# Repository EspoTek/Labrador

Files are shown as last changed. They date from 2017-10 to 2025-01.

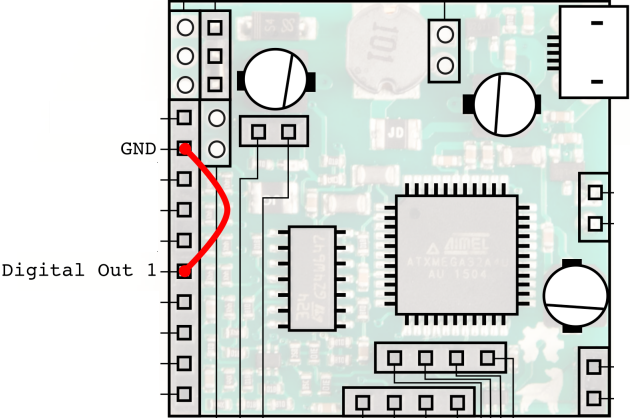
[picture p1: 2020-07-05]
Desktop_Interface/diagram.png

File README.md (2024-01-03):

# What is it?
The [EspoTek Labrador](http://espotek.com/labrador) is an open-source board that turns your PC, Raspberry Pi or Android Smartphone and into a full-featured electronics lab bench, complete with oscilloscope, signal generator and more.

This repo hosts all of the software and hardware that makes Labrador possible.

# Tutorial
If you're new to Labrador or oscilloscopes in general, I strongly recommend checking out the fantastic tutorial series produced by Lief Koepsel:   
https://www.wellys.com/posts/courses_electronics/  
It features well-written, rich articles as well as video content that explains everything more clearly than I ever could!  

# Getting Started
To download binary (executable) versions of the software, go to:  
https://github.com/espotek/labrador/releases

For the documentation, please visit:  
https://github.com/espotek/labrador/wiki 

# Raspberry Pi Build
***Please note that the 32-bit version of Raspbian version 9 (Stretch) or later is required to install this software.***

To install Labrador on the Raspberry Pi, open a terminal and paste the following command:  
`wget -O /tmp/labrador_bootstrap_pi https://raw.githubusercontent.com/EspoTek/Labrador/master/labrador_bootstrap_pi && sudo chmod +x /tmp/labrador_bootstrap_pi && sudo /tmp/labrador_bootstrap_pi`

This will automatically download, compile and install the latest version of the Labrador software from source.  The whole process will take around 20-30 minutes, so don't forget to pack a snack!  
After running it, a desktop entry will appear for the Labrador software (under Education), and running the `labrador` command from the terminal will launch the software interface.

# Additional Extras
There are community contributed 3D printable cases available at Thingiverse, courtesy of SpaceBex and Bostwickenator:
* https://www.thingiverse.com/thing:3188243
* https://www.thingiverse.com/thing:4705392

* Dave Messink has designed [a case that can be laser cut from 3mm plywood](https://github.com/EspoTek/Labrador/files/13813693/Re__Labrador_Case.1.zip)  
The binding posts and cables he used are from Amazon.  
https://www.amazon.com/dp/B07YKYP8MN?psc=1&ref=ppx_yo2ov_dt_b_product_details  
https://www.amazon.com/dp/B08KZGPTLM?ref=ppx_yo2ov_dt_b_product_details&th=1  
https://www.amazon.com/dp/B08KZGPTLM?ref=ppx_yo2ov_dt_b_product_details&th=1  



# Building from Source
If you're looking to build from source but don't know where to start, Qt Creator is the easiest way to get your toes wet!  
https://www.qt.io/download-open-source/  
When installing, make sure you tick the box to install Qt 5.15 or later.

Once it's installed, open Desktop_Interface/Labrador.pro, then Clean All -> Run qmake -> Build All.

If you're on Linux (including Raspberry Pi), then you can also build the software from source by cloning the repo, cd'ing to the Desktop_Interface directory then running:  
```
qmake
make
sudo make install
```
Then, to launch, just type `labrador` into the terminal.

On Macos, additional steps may be required.  See issue https://github.com/EspoTek/Labrador/issues/238

To build the AVR software, I use Atmel Studio 7.  Just load up the .atsln and push F7.  You can use `avr-gcc` if you don't want to install a full IDE.

The PCB files can be edited in KiCAD 5.0 or later.

# Licence
All Dekstop software files are licenced under GNU GPL v3.  https://www.gnu.org/licenses/gpl.html

All Microcontroller software files, with the exception of those provided by Atmel, are licenced under the 3-Clause BSD License.  https://opensource.org/licenses/BSD-3-Clause

All hardware files (schematics, PCB) are licenced under Creative Commons 4.0 (CC BY-NC-SA).  https://creativecommons.org/licenses/by-nc-sa/4.0/

# Collaboration
If you want to submit a Pull Request, bug report or feature request please feel free to do so here at GitHub.  
If you just want to say hello and remind me that people are actually using my product (or if you just don't want to make a GitHub account), please email admin@espotek.com

Thanks to all.  
~Chris

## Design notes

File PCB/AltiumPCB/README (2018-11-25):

Altium PCB designed by Ele4nor based on the original EspoTek KiCAD design.

This is just a prototype design optimized for homemade pcb fabrication.
The pcb design and BOM is different from "Tinylab_proto1", but the schematic is mostly Compatible.
Note that the small designators are NOT ideal and they're there for pdf only reference.
nevertheless it has been tested and functions properly but you need to program atmel usb dfu bootloader first to allow firmware flashing from Desktop App.
Use of the crystal oscillator is optional and requires firmware modification.

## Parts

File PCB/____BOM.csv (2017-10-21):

Id | Designator | Package | Quantity | Designation | Description | Notes
1 | C6,C9,C15 | c_elec_4x5.3 | 3 | CP1 | SMD Electrolytic Capacitor, 33uH 16V
2 | IC1 | LQFP-44_10x10mm_Pitch0.8mm | 1 | ATXMEGA32A4U-A | ATXMEGA32A4U-AU
3 | P2 | USB_Micro-B_WIDE | 1 | USB_OTG | Micro USB-B connector
5 | C1,C2,C7,C8,C10,C11,C13,C14,C16,C17,C18 | C_0603 | 11 | C | 1uF 0603 Ceramic Cap
6 | C3,C4,C5 | C_0603 | 3 | C_Small | 1uF 0603 Ceramic Cap
7 | D1 | SMA_Standard | 1 | D_Schottky | SMA Schottky Diode, 1.5V 1A
8 | D2 | LED_0603 | 1 | LED | 0603 LED
9 | F1 | C_1210 | 1 | F_Small | PTC Fuse
10 | L1 | SELF-WE-PD-XXL | 1 | INDUCTOR | SMD Inductor (self-wound package)
11 | L2,L3,L4 | R_1206 | 3 | INDUCTOR | SMD Inductor 1206
4 | P1,P5 | Pin_Header_Straight_1x04 | 2 | SCOPE_OUT | Female 1x4 header
12 | P3 | Pin_Header_Straight_1x04 | 1 | DIG_OUT | Stackable 1x10 Header | P3, P4 and P4 share a single header. Please do not use flimsy/weak pins!
14 | P6 | Pin_Header_Straight_1x04 | 1 | DAC_OUT | Stackable 1x10 Header | P3, P4 and P4 share a single header. Please do not use flimsy/weak pins!
13 | P4 | Pin_Header_Straight_2x02 | 1 | PDI/3V3 | Stackable 1x10 Header | P3, P4 and P4 share a single header. Please do not use flimsy/weak pins!
 | P7 | Pin_Header_Straight_1x02 | 1 | PSU | Stackable 1x2 Header | “Stackable” refers to the pins that are female on one side and male on the other, like on many Arduino shields.
16 | P8 | Pin_Header_Straight_1x02 | 1 | DIG_IN | Female 1x2 Header
17 | P10 | Pin_Header_Straight_1x03 | 1 | EXPANSION | - | Unpopulated
18 | P11 | Pin_Header_Straight_1x03 | 1 | SWITCH | Male 1x3 Header
26 | REF** | Pin_Header_Straight_1x02 | 1 | Pin_Header_Straight_1x02 | Male 1x2 Header | This will need to be soldered on upside down
19 | Q1 | SOT-23-3 | 1 | Q_NMOS_GSD
20 | R1,R2,R3,R4,R5,R6,R15,R16,R17,R18,R19,R20,R21,R22,R23,R24,R25,R26,R27,R28,R29,R30,R31 | R_0603 | 23 | R
21 | R7,R8,R9,R10,R11,R12,R13,R14 | R_0603 | 8 | 28R
22 | R32 | R_0603 | 1 | R_Small
23 | U1 | SOT-23-3 | 1 | 78L05
24 | U2 | SOIC-14_3.9x8.7mm_Pitch1.27mm | 1 | LM324
25 | U3,U4 | SOT-363 | 2 | DMN63D8LDW

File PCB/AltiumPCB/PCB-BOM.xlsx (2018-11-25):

Comment | Description | Designator | Footprint | LibRef | Quantity
Atxmega32A4U-AN |  |  | QFP44P80_1200X1200X120L60X37N | Atxmega32A4U-AN | 1
1µF | 1µF 25V Ceramic Capacitor X5R 0805 (2012 Metric) 0.079" L x 0.049" W (2.00mm x 1.25mm) | C1, C2, C3, C4, C5, C6, C11, C12, C18, C19, C20 | CAPC200X125X75L45N | 885012107015 | 11
1nF | 1000pF 16V Ceramic Capacitor X7R 0805 (2012 Metric) 0.079" L x 0.049" W (2.00mm x 1.25mm) | C7 | CAPC200X125X75L45N | 885012207033 | 1
0.47µF | 0.47µF 10V Ceramic Capacitor X7R 0805 (2012 Metric) 0.079" L x 0.049" W (2.00mm x 1.25mm) | C8, C13 | CAPC200X125X75L45N | 885012207020 | 2
0.10µF | 0.10µF 10V Ceramic Capacitor X7R 0805 (2012 Metric) 0.079" L x 0.049" W (2.00mm x 1.25mm) | C9, C21 | CAPC200X125X75L45N | 885012207016 | 2
4.7µF | 4.7µF 16V Ceramic Capacitor X5R 0805 (2012 Metric) 0.079" L x 0.049" W (2.00mm x 1.25mm) | C10 | CAPC200X125X75L45N | 885012107013 | 1
20pF | CAP CER 20PF 50V NP0 0805 | C14, C15 | CAPC200X125X75L45N | CL21C180JBANNNC | 2
CAP_POLAR | Aluminium Electrolyte 16V max | C16, C17 | Cap_Elec_47uF | CAP_POLAR | 2
FM5819-W | Schottky Diodes & Rectifiers Vr/40V Io/1A T/R | D1 | DIOM470X266X220L114X139N | FM5819-W | 1
RED | LED RED DIFFUSED 0805 SMD | D2 | LEDC200X125X38L45N | LH R974-LP-1 | 1
AO6802 | MOSFET 2N-CH 30V 3.5A 6-TSOP | IC1, IC2 | ALPHAOMEGA TSOP-6 |  | 2
Micro USB | CONN USB MICRO B RECPT SMT R/A | J1 | FCI USB 10118193-0001LF |  | 1
Jumper |  | J3, J4 | RESC200X125X50L35N |  | 2
22uH | Fixed Inductor 22uH 20% 165mA | L1, L3, L4 | CAPC200X125X140L45N | LBC2016T220M | 3
100uH | FIXED IND 100uH 400MA 1.26 OHM | L2 | CD54-Modified | CD75NP-331KC | 1
Expansion | Header, 3-Pin | P0 | HDR1X3 | Header 3 | 1
SCOPE_OUT | Header, 4-Pin | P1, P5 | HDR1X4 | Header 4 | 2
DIG_OUT | Header, 4-Pin | P3 | HDR1X4 | Header 4 | 1
PDI | Header, 4-Pin | P4 | HDR1X4 | Header 4 | 1
DAC_OUT | Header, 6-Pin | P6 | HDR1X6 | Header 6 | 1
PSU | Header, 2-Pin | P7 | HDR1X2 | Header 2 | 1
DIG_IN | Header, 2-Pin | P8 | HDR1X2 | Header 2 | 1
SWITCH | Header, 3-Pin | P11 | HDR1X3 | Header 3 | 1
2N7002 | MOSFET N-CH 60V 0.115A SOT-23 | Q1 | SOT23-3P95_230X110L30X43N | 2N7002LT1G | 1
1K | RES SMD 1K OHM 1% 1/8W 0805 | R1, R4, R5, R8, R11, R12, R13, R14, R17, R18, R19, R20, R29, R30, R31 | RESC200X125X50L35N | RC0805FR-071KL | 15
1M | RES SMD 1M OHM 5% 1/8W 0805 | R2, R7 | RESC200X125X50L35N | RC0805JR-071ML | 2
75K | RES SMD 75K OHM 1% 1/8W 0805 | R3, R6 | RESC200X125X50L35N | RT0805FRE0775KL | 2
28R | RES SMD 28 OHM 1% 1/10W 0603 | R9, R10, R15, R16, R21, R22, R23, R24, R25, R26, R27, R28 | RESC160X80X55L25N | RC0603FR-0728RL | 12
100R | YAGEO RC0805JR-07100RL RES, THICK FILM, 100R, 5%, 0.125W, 0805 | R32 | RESC200X125X50L35N | RC0805JR-07100RL | 1
AMS1117-3.3 | Linear Reg 3.3, 1.2V dropout | U1 | SOT223-4P229_700X180L36X74N | AMS1117-3.3 | 1
LM324 | IC OPAMP GP 14SOIC | U2 | SOIC14P127_865X600X175L83X41N | LM324MX | 1
8MHz | Crystals 8MHz 20pF | Y1 | TXC 9C | ATS08ASM-1 | 1

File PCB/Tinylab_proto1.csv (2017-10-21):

Reference | Value | Footprint | Datasheet
C1 | SMD MLCC 1uF 16V 0603 | Capacitors_SMD:C_0603
C2 | SMD MLCC 1uF 16V 0603 | Capacitors_SMD:C_0603
C3 | SMD MLCC 1uF 16V 0603 | Capacitors_SMD:C_0603
C4 | SMD MLCC 1uF 16V 0603 | Capacitors_SMD:C_0603
C5 | SMD MLCC 1uF 16V 0603 | Capacitors_SMD:C_0603
C6 | SMD 4mm 33uF | Capacitors_SMD:c_elec_5x5.3
C7 | SMD MLCC 1uF 16V 0603 | Capacitors_SMD:C_0603
C8 | SMD MLCC 1uF 16V 0603 | Capacitors_SMD:C_0603
C9 | SMD 4mm 33uF | Capacitors_SMD:c_elec_4x5.3
C10 | SMD MLCC 1uF 16V 0603 | Capacitors_SMD:C_0603
C11 | SMD MLCC 1uF 16V 0603 | Capacitors_SMD:C_0603
C13 | SMD MLCC 1uF 16V 0603 | Capacitors_SMD:C_0603
C14 | SMD MLCC 1uF 16V 0603 | Capacitors_SMD:C_0603
C15 | Thru Hole 6.3mm 220uF | Capacitors_ThroughHole:C_Radial_D6.3_L11.2_P2.5
C16 | SMD MLCC 1uF 16V 0603 | Capacitors_SMD:C_0603
D1 | Thru Hole Schottky 1A | Diodes_ThroughHole:Diode_DO-41_SOD81_Horizontal_RM10
F1 | SMD PTC 400mA | Capacitors_SMD:C_1206
IC1 | QFN ATXMEGA16A4U-A | Housings_QFP:LQFP-44_10x10mm_Pitch0.8mm
L1 | Thru Hole Radial 220uH | Inductors:INDUCTOR_V
L2 | SMD 10uH 1210 | Resistors_SMD:R_1210
L3 | SMD 10uH 1210 | Resistors_SMD:R_1210
P1 | Female Header 1x2 | Pin_Headers:Pin_Header_Straight_1x02
P2 | Micro USB-B Connector (F) | Connect:USB_Micro-B_WIDE
P3 | Male header 1x4 | Pin_Headers:Pin_Header_Straight_1x04
P4 | Male header 2x2 | Pin_Headers:Pin_Header_Straight_2x02
P5 | Female Header 1x2 | Pin_Headers:Pin_Header_Straight_1x02
P6 | Male header 1x4 | Pin_Headers:Pin_Header_Straight_1x04
P7 | Male header 1x2 | Pin_Headers:Pin_Header_Straight_2x02
P8 | Feamle Header 1x2 | Pin_Headers:Pin_Header_Straight_1x02
P9 | Female Header 1x2 | Pin_Headers:Pin_Header_Straight_1x02
P10 | Female Header 1x2 | Pin_Headers:Pin_Header_Straight_1x02
Q1 | SMD nMOS Transistor TSM2302CX | SMD:SOT-23-3
R1 | SMD 1M? 20V 0603 | Resistors_SMD:R_0603
R2 | SMD 1M? 20V 0603 | Resistors_SMD:R_0603
R3 | SMD 75k? 6.3V 0603 | Resistors_SMD:R_0603
R4 | SMD 75k? 6.3V 0603 | Resistors_SMD:R_0603
R5 | SMD 1k? 16V 0603 | Resistors_SMD:R_0603
R6 | SMD 1k? 16V 0603 | Resistors_SMD:R_0603
R7 | SMD 28? 6.3V 0603 | Resistors_SMD:R_0603
R8 | SMD 28? 6.3V 0603 | Resistors_SMD:R_0603
R9 | SMD 28? 6.3V 0603 | Resistors_SMD:R_0603
R10 | SMD 28? 6.3V 0603 | Resistors_SMD:R_0603
R11 | SMD 28? 6.3V 0603 | Resistors_SMD:R_0603
R12 | SMD 28? 6.3V 0603 | Resistors_SMD:R_0603
R13 | SMD 28? 6.3V 0603 | Resistors_SMD:R_0603
R14 | SMD 28? 6.3V 0603 | Resistors_SMD:R_0603
R15 | SMD 1k? 16V 0603 | Resistors_SMD:R_0603
R16 | SMD 1k? 16V 0603 | Resistors_SMD:R_0603
R17 | SMD 1k? 16V 0603 | Resistors_SMD:R_0603
R18 | SMD 1k? 16V 0603 | Resistors_SMD:R_0603
R19 | SMD 1k? 16V 0603 | Resistors_SMD:R_0603
R20 | SMD 1k? 16V 0603 | Resistors_SMD:R_0603
R21 | SMD 100? 16V 0603 | Resistors_SMD:R_0603
R22 | SMD 28? 6.3V 0603 | Resistors_SMD:R_0603
R23 | SMD 28? 6.3V 0603 | Resistors_SMD:R_0603
R24 | SMD 28? 6.3V 0603 | Resistors_SMD:R_0603
R25 | SMD 28? 6.3V 0603 | Resistors_SMD:R_0603
R26 | SMD 1k? 16V 0603 | Resistors_SMD:R_0603
R27 | SMD 100? 16V 0603 | Resistors_SMD:R_0603
R28 | SMD 100? 16V 0603 | Resistors_SMD:R_0603
R29 | SMD 100? 16V 0603 | Resistors_SMD:R_0603
R30 | SMD 100? 16V 0603 | Resistors_SMD:R_0603
U1 | SMD 3.3V Reg RT9161A-33GV | SMD:SOT-23-3
U2 | SMD LM324 | Housings_SOIC:SOIC-14_3.9x8.7mm_Pitch1.27mm
U3 | SMD DMN63D8LDW | TO_SOT_Packages_SMD:SOT-363
U4 | SMD DMN63D8LDW | TO_SOT_Packages_SMD:SOT-363

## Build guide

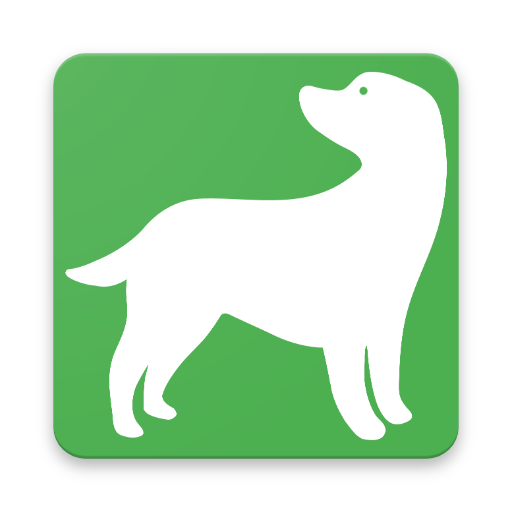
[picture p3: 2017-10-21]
Desktop_Interface/build_android/package_source/res/web_hi_res_512.png

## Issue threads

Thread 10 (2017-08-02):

### ISSUE TITLE
Make the PCB a little more breadboard compatible?

### ISSUE THREAD

**Issue by tardate** [EspoTek/Labrador#10]
I've been playing with a batch 1 backer edition PCB (you can [see my notes here](https://github.com/tardate/LittleArduinoProjects/tree/master/Equipment/Labrador)).

I was able to stick it on a breadboard with a minor bend of the PSU pins, and then the PSU is on the breadboard power rail and all the pins on the left side of the board are routed to the breadboard. This is pretty convenient for testing and experimentation.

Although the board will never be fully breadboard-compatible in its current form, there's one minor change that might be worth considering: nudge the PSU pins up or down 50mil and then the PCB would plug directly into a standard MB104 breadboard with no pin bending.

**Comment by EspoTek** [comment]
You're absolutely right.   I didn't actually believe you until I tried it myself!
The fact that the pins bend when being plugged into a breadboard is definitely a bug.  Fortunately not a critical one, but still not ideal...  It was designed to go in smoothly; I even used a 50mil grid to ensure it was perfectly accurate.  Looks like at some stage that grid god messed up, though.

I'll have to fix that up for the next batch (also will ensure they use a better opamp to reduce noise a bit).

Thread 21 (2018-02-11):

### ISSUE TITLE
Feature request: Enable data storage in Android app

### ISSUE THREAD

**Issue by drtrigon** [EspoTek/Labrador#21]
Please add data recording/storage/logging to the Android app, would that be possible?

(edit: what about the power supply features - could them be added too?)

**Comment by EspoTek** [comment]
Power supply and data storage functions are actually all in the software.  I just hide the buttons to activate them on Android.

The reason I did this is because of the small memory on most phones.  8GB free space or less is very common, and that would fill up with something like 10-15 mins of recording.

The power supply option is disabled since USB OTG is specced for 100mA only, and most of that would be eaten up just by the board itself.  I think I calculated 65mA with no signal generator or power supply load, leaving only 35mA for the power supply (which would be almost completely lost in the switching circuitry).

That being said, I plan on improving the DAQ features of Labrador, and once that's in then I'll be able to add the data storage back into Android.
I'll be working on it during the week after Christmas.

Enabling the power supply is not really an option, though.

**Comment by ajxn** [comment]
Maybe give a short not about this in a About message dialog?

**Comment by drtrigon** [comment]
> The reason I did this is because of the small memory on most phones. 8GB free space or less is 
> very common, and that would fill up with something like 10-15 mins of recording.

What about a screenshot feature; store the contents of the display - e.g. single trigger - as png or csv?

What about an expert feature that unhides the hidden features with a warning about the issues.

> The power supply option is disabled since USB OTG is specced for 100mA only, and most of that 
> would be eaten up just by the board itself. I think I calculated 65mA with no signal generator or 
> power supply load, leaving only 35mA for the power supply (which would be almost completely lost 
> in the switching circuitry).

I assumed something like that... that's a pitty because it would be useful not as a current source but signal voltage source, e.g. for testing a ADC port (drawing microamps).

> That being said, I plan on improving the DAQ features of Labrador, and once that's in then I'll be 
> able to add the data storage back into Android.
> I'll be working on it during the week after Christmas.

Great news, perfect! Will be a very nice (Christmas) gift!

**Comment by EspoTek** [comment]
The screenshot feature is also already in there.  It's hidden on Android too, but I can't offer a good explanation why...

I could enable an "Expert Mode" that turns on all of the features, and it could pop up with ajxn's "About" message that warns the user when you click it!

**Comment by drtrigon** [comment]
Can you give an assumption when the new updated app will be available?

**Comment by EspoTek** [comment]
When I get around to it.  ;)
Should be soon.

Have quit the PhD and so will be unemployed as soon as I finish a piece of software for the honours students.  We have a neurosignal amplifier only runs on a single PC that runs Windows XP and requires a DRM dongle.  I managed to reverse-engineer the protocol, but now that needs to be turned into an API.
Then, it's Labrador time.  :)

**Comment by EspoTek** [comment]
It's live.
You should get a notification from Google Play soon.

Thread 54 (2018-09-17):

### ISSUE TITLE
Nice to have; more sophisticated scaling options

### ISSUE THREAD

**Issue by drtrigon** [EspoTek/Labrador#54]
As we have the scaling options on the main window now it would be really really nice to polish them a bit.
1. up and down arrows should change the decimal place the cursor is (currently it just in- or decrements by 1.0 volt or second which is most of the time way to much)
2. may be add sliders or knobs that resemble more the look and feel of a desktop scope (don't know what the GUI toolkit/framework offers)

This is not a bug but a nice to have feature of low priority. Thanks.

**Comment by EspoTek** [comment]
I've actually got a class that does point number one already; its the one used in the Signal Generator inputs (which honestly could use a bit of a spit-polish too).  Changing this should be pretty easy.

Honestly not keen on sliders or knobs on the main screen, though.  One of the selling points is that it doesn't have them!  I've used the Hantek software before, which tried to simulate the interface of a "real" scope and honestly it was just really clunky.

**Comment by EspoTek** [comment]
Check the latest patch.  The changes I made also improved the signal generator controls and the pop-up dialog.

Let me know what you think.
For now, I'm very happy with everything (although a "time minimum" and "time max" might be better than "time window" and "delay".

I'm closing this issue for now, as I don't think more controls are necessary.  You already have direct range controls on the front page, after all.  :)

**Comment by drtrigon** [comment]
Thanks for your work! Hmmm - honestly to me it is a bit confusing ... but it might be that I am not used to it yet. It is smoother and makes more sense when you are looking for a signal you don't know the scaling yet. May be a little confusing is the fact the when is written "500mV" I actually have to enter "0.5[ENTER]". Let me work with it for some time... It is clearly better that before.

One thing you should check the behaviour for negative values, crossing "-1.0V" and values below does not work properly. I also had other strange issues. E.g. if I put the cursor into the field "-500mV" (which is default when starting) and hit [ENTER] it changes to "500mV" (positive).

**Comment by EspoTek** [comment]
You should be able to type in "500m[ENTER]" to get 500mV.  I just tested it in my machine and that was the case.

Issue with negative numbers noted.  There's an internal variable keeping track of the last known correct input that is not being updated correctly (with sign).  I'll fix this and patch now.

**Comment by EspoTek** [comment]
Oh, and one last thing: regarding why you must press enter now:
Say the user wants to enter "500mV".  They type in 5, then 0, 0, m.

If you recalculate the scale on every keypress, it first goes to 5V, then 50V (which goes down to the maximum of 20V because it's invalid), then 200V (which again is reduced to 20V to stay within the valid range), then 20mV.  That is not 500mV.

If you're just trying to get a rough estimate and don't need to be precise, I'd recommend using the mouse scrolling.

**Comment by drtrigon** [comment]
> You should be able to type in "500m[ENTER]" to get 500mV. I just tested it in my machine and that was the case.

You are right - guess I entered "500mV[ENTER]" not beeing aware that the "V" stays there and then it jumps to 20V... ;)

Having to press enter is ok and makes sense - I don't like the updates on every keypress (exactly due to issues you describe - some value need more than 1 char to be expressed...)

> If you're just trying to get a rough estimate and don't need to be precise, I'd recommend using the mouse scrolling.

I was not aware of mouse scrolling (now I even got my "knob")! This is great; very useful and fast!!

> I have fixed the issue with negative values. It now uses std::abs() to compare work out the units and scale things, as opposed to the weird hack it was using before.

Thanks for this, however still some non-intuitive things happening here:
- if I press enter in the field the result heavily depends on the cursor position before pressing enter - I assume only the value in front of the cursor is used (e.g. if I put the cursor behind the 5 of -500mV I do get -5V)
- if I start scrolling with the mouse wheel downwards (starting from -500mV) it does 1V steps - I think this is just an issue of a missing init step
- if I start scrolling upwards the same for one step (+1V to 500mV) then it behaves as expected - seems to be sign dependent
- if I try to scroll down from 500mV (passing 0) it stops working at 90mV and the only way to make it work again is entering a value by keyboard

**Comment by EspoTek** [comment]
Wow.  And that's why you don't write code on the train after a day of work while sleep deprived!

I've fixed all of the bugs you mentioned, done some more testing to try and find others and it looks like it's all fixed now.  The error regarding the very small (near-zero) number is an issue with floating point precision.  I won't launch into the details, but it's basically a weird, weird form of rounding error.  I've seen an example of it once where a guy managed to get the result 1 + 1 = 3!

**Comment by drtrigon** [comment]
What I tested seems to work nicely now even "10us" works - cool, thanks!

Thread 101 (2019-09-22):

### ISSUE TITLE
Cannot See Device When Plugged In (Mac 10.14.8, RPi Zero)

### ISSUE THREAD

**Issue by joedski** [EspoTek/Labrador#101]
Hello, I am not seeing my Labrador when I plug it into my computer.  I have tried the following, both with nothing shorted and in bootloader mode.

- Mac 10.14.8 on 2012 MBP:
   - USB 2 port directly on computer
   - USB 3 port on dock
- Raspberry Pi Zero W:
   - Data-enabled USB port
   - Data-enabled USB port via USB 2 hub, Labrador as only device plugged into the hub

Across all of the above, I've tried:

- In bootloader mode
- Not in bootloader mode

Using `lsusb` did not show any changes before and after plugging the device in.  The power LED does turn on, but I don't see anything else happen anywhere.  I've ensured that the cable I used can transmit data, as I have used it to interface with a NodeMCU board.

Is there anything else I could try that I might have missed in the docs?

**Comment by EspoTek** [comment]
If `lsusb` shows no change and the cable can transfer data, then the only possible explanation is that your board is DOA.

Please contact me at `admin@espotek.com` with your order info and I'll have a replacement shipped out to you free of charge.

And thanks for being descriptive with all the troubleshooting steps - no back and forth this way.

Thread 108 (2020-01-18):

### ISSUE TITLE
higher sample rate to see adressable LED data. SPI, I2C, Serial.

### ISSUE THREAD

**Issue by perigalacticon** [EspoTek/Labrador#108]
This would be a perfect device to use to diagnose addressable led data such as WS2812B, but it runs at 800kHz.  Can't tell you how many times I wanted to get a good look at what is causing glitching in certain installations.  Having a small battery or 5V powered portable scope would be great for this.  Not sure how fast you need to sample to get 800kHz but that would be really nice.

**Comment by EspoTek** [comment]
Try Labrador's logic analyzer.  It works exactly like the oscilloscope, but takes 3 million samples per second (so you'd get 3-4 samples per bit at 800kHz!)

The downside is that each sample is only one bit - so you can't see the exact analog waveform of the signal, just if it's on or off.

If you need that level of detail in a portable device, I've heard nothing but positive things about Picoscope's products:
https://www.picotech.com/
They're obviously a bit more than $29, though!

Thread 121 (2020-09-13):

### ISSUE TITLE
taking samples for both channels simultaniously via librador

### ISSUE THREAD

**Issue by jhegedus42** [EspoTek/Labrador#121]
Hi,

I am able to get samples from a single chanell using a single octave call via librador.

Now, the question is ... how can I get samples for two channels ?

I am trying to understand this : https://github.com/EspoTek/Labrador/blob/e7c5e4e68768f87d1df8cc61be07e32e3b8d232e/Librador_API/___librador/librador_shared_library/o1buffer.cpp

and this : 

but its not easy ... 

https://github.com/EspoTek/Labrador/blob/e7c5e4e68768f87d1df8cc61be07e32e3b8d232e/Librador_API/___librador/librador_shared_library/usbcallhandler.cpp

maybe if I could modify this : https://github.com/EspoTek/Labrador/blob/e7c5e4e68768f87d1df8cc61be07e32e3b8d232e/Librador_API/___librador/librador_shared_library/usbcallhandler.cpp#L313

to do something like this : https://github.com/EspoTek/Labrador/blob/e7c5e4e68768f87d1df8cc61be07e32e3b8d232e/Librador_API/___librador/librador_shared_library/usbcallhandler.cpp#L76

but what is isocallback ? I am really sorry for all these dumb questions but C/C++ is something I never was able to 
learn :( ... I try to read the code... but it's difficult.

can someone please point me into the right direction ? Please ?
 
I am really lost here ... :(

Thanks,

Jozsef

**Comment by phr0gger** [comment]
I have some python code to configure the Labrador board and to read back data.
Would that help you?

**Comment by EspoTek** [comment]
When the device is set to mode 4, the latter 375 bytes of the each packet contain the data for CH2.
https://docs.google.com/document/d/1ZDO1RTarQTNB6Pdfi_T4YukL51oYan_kk_teb1cu6-o/edit#heading=h.3v1s22knpngz

**Comment by jhegedus42** [comment]
> I have some python code to configure the Labrador board and to read back data.
> Would that help you?

Thank you that would be great, is it on github ? I check your code now.  Maybe it is already there.

**Comment by phr0gger** [comment]
I don't think my code is GitHub-worthy.
Below is what I did on my Raspi to read and plot data from the Labrador board with Python 3.7. It is based on the sample code by Vincent Pelletier, who wrote the python-libusb1 package which you need for the asynchronous support.
PyUSB does not support asynchronous isochronous transfers.

`import usb1  # python-libusb1 package from 
from struct import unpack
import sys
import time
import numpy as np
import matplotlib.pyplot as plt

MODE = 0  # Labrador mode ( 7: 12 bit 375 ksps, 6: 8 bit 750 ksps, 0: 8 bit 375 ksps)
SHOW = 20*750

VENDOR_ID = 0x03eb
PRODUCT_ID = 0xba94
INTERFACE = 0
TIMEOUT = 100

GAIN = 0x0808  # gain 4: ±6V
#GAIN = 0x0c0c  # gain 8: ±3V

ISO_EP = 0x81
NUM_ISO_PACKETS = 66
ISO_PACKET_SIZE = 750
TRANSFER_COUNT = 4

def processReceivedData(trf):
    global stream
    global t0
    if MODE == 7:
        dt = np.dtype(np.int16)
        dt = dt.newbyteorder('<')  # big endian
    else:
        dt = np.dtype(np.int8)
    t1 = time.monotonic()
    if trf.getStatus() != usb1.TRANSFER_COMPLETED:  # TRANSFER_COMPLETED = 0 
        # Transfer did not complete successfully, there is no data to read.
        # This example does not resubmit transfers on errors. You may want
        # to resubmit in some cases (timeout, ...).
        print(' Error: Transfer not completed successfully!')
        return
    stream.extend( np.frombuffer(trf.getBuffer(), dtype=dt)) 
    #stream.extend( trf.getBuffer())  # raw hex stream
    # trf.getActualLength() useless for isochronous (always 0)
    print(f' time: {1000*(t1-t0):3.2f}')  
    # Resubmit transfer once data is processed for endless process
    #transfer.submit()
    t0 = t1

stream = []
with usb1.USBContext() as context:
    context = usb1.USBContext()
    handle = context.openByVendorIDAndProductID(
        VENDOR_ID,
        PRODUCT_ID,
        skip_on_error = True,
    )
    if handle is None:  # Device not present, or user is not allowed to access device.
        print('Error: Cannot find Labrador Board!')
        sys.exit()
    else:
        print('Found', handle.getManufacturer(), handle.getProduct())
        print(' FW Version :', unpack('H',handle.controlRead(0xc0,0xa8,0,0,2,TIMEOUT))[0])
        print(' FW Variant :', handle.controlRead( 0xc0, 0xa9, 0, 0, 1, TIMEOUT)[0])
            
    with handle.claimInterface( INTERFACE):  # Required to receive/send data.
        handle.controlWrite( 0x40, 0xa5, MODE, GAIN, b'', TIMEOUT) #
        handle.controlWrite( 0x40, 0xa6, 0, 0, b'', TIMEOUT)  # turn off digital pins
        handle.controlWrite( 0x40, 0xa4, 0, 0, b'', TIMEOUT)  # disable DAC amp
        handle.controlWrite( 0x40, 0xa3, round(6/18.15*128)-1, 0, b'', TIMEOUT)  # set 6V

        # Build a list of transfer objects and submit them to prime the pump.
        transfer_list = []
        for i in range( TRANSFER_COUNT):
            print( ' Starting transfer',i)
            transfer = handle.getTransfer( NUM_ISO_PACKETS)  # libusb_alloc_transfer
            transfer.setIsochronous(                         # libusb_fill_iso_transfer
                ISO_EP,
                NUM_ISO_PACKETS*ISO_PACKET_SIZE,             # 
                callback = processReceivedData,
            )                                                # default is no timeout
            transfer.submit()                                # libusb_submit_transfer
            transfer_list.append(transfer)
        print()
        t0 = time.monotonic()
        # Loop as long as there is at least one submitted transfer.
        while any(x.isSubmitted() for x in transfer_list):
            try:
                context.handleEvents()                      # libusb_handle_events
            except usb1.USBErrorInterrupted:
                pass
if MODE == 7:
    data = -np.right_shift( stream, 4)[:SHOW]
elif MODE == 6:
    #data = list(map(lambda x: -x, stream[:SHOW]))
    data = stream[:SHOW]
elif MODE == 0:
    data = np.reshape(stream[:2*SHOW],(4*SHOW//750,375))[::2].ravel()
fig, ax = plt.subplots(figsize = (12, 7))
ax.plot( data, '.', markersize = 2)
ax.set_xticks(range(0,len(data)+1,375))
ax.grid()
ax.set_title( f'Mode: {MODE}, Gain: 0x{GAIN:04X}')
fig.tight_layout()
plt.show()  
`

**Comment by jhegedus42** [comment]
Thank you !

It seems to work !

![image](https://user-images.githubusercontent.com/6671476/87711164-31f7a300-c7a7-11ea-9e61-ad9f7b5fce40.png)

**Comment by jhegedus42** [comment]
> I don't think my code is GitHub-worthy.
> Attached is what I did on my Raspi to read and plot data from the Labrador board with Python 3.7. It is based on the sample code by Vincent Pelletier, who wrote the python-libusb1 package which you need for the asynchronous support. Note, that PyUSB does not support asynchronous isochronous transfers, read and write are blocking.


Would it be ok to use blocking calls?

C itself is blocking - if using Librador.

Why is it good to use async lib?

I mean, why is it bad if one python process is blocking?

I plan to use TCP/IP to transfer packets read from Labrador to Simulink/GNURadio, that can be blocking, python runs in separate process.

I did this already with UDP packets using Librador library from C. It worked for one channel. Using python seems to be easier though.

But do I need async calls for that?

It just worked fine with Librador + blocking calls to libusb + C + UDP + Simulink + FIFO (buffer).

Is async USB transfer with callbacks any better than blocking calls ?

It seems more complicated.  

Is the Labrador QT GUI using async USB calls or just using blocking USB calls + buffer + 2 threads (one for GUI and one for USB transfers).

Cheers,

Jozsef

**Comment by EspoTek** [comment]
I think I can answer that question, Joszef.

The GUI code uses async isochronous USB (but synchronous everything else), and the main advantage of this is no data loss when streaming.
The board itself only stores the previous 1ms of data in SRAM, so in order to extract every sample it must be polled every single USB frame - no exceptions.
This is impossible to guarantee with synchronous communications, as there is some downtime between packets being received and packets requested.
The flow looks something like this:
 1) Request _n_ frames of data
 2) Data received 
 3) Process data
 4) Goto 1
If steps 2 and 3 take longer than 1ms, you lose continuity.

With async, you can immediately queue a second (future) request after the first request is submitted.  Then, when the first request is complete, you can schedule a third before the second completes (and so on...).  This way you don't lose continuity.

Try looking at an odd frequency (I like 912Hz) and you'll see what I'm talking about.  You'll get a discontinuity every `NUM_ISO_PACKETS` samples.

(Apologies if that made no sense.  I just became a father on Saturday and haven't had a nights' sleep since)

**Comment by jhegedus42** [comment]
Dear Chris,

First of all. I wish you and your family health and happiness !

Thank you for the help. It is very good to know this. It's not trivial to make such a 
little device work. I start to understand that.

I rather ask now @phr0gger ... he may not be so busy now.

Is there a way to make this record data continously ?
The python code that you attached, @phr0gger  ?

What does it mean 
"  # Build a list of transfer objects and submit them to prime the pump."


"prime the pump" ?

Do you mean bootstrap ?

I was thinking I should uncomment this line : 

```
    # Resubmit transfer once data is processed for endless process
    #transfer.submit()
```
but it just died...

or did not really work...

what should I do if I want to continously capture data and, say, send them over
TCP/IP or just save to file ?

Cheers,

Jozsef

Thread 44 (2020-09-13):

### ISSUE TITLE
DataLogger for Education

### ISSUE THREAD

**Issue by drtrigon** [EspoTek/Labrador#44]
As requested in #37 a new issue:

>> Another point here is; if the device would be a bit more fool-prove and the software a bit more intuitive to use (e.g. "beginner" mode) we could use it in schools for education (for teenagers, ~14yrs). Again all concurring products are about 10 times the price of a labrador. At least I would be immediately willing of ordering 10 to 20 devices for one school I am working at. :)
> 
> Drtigon, the hardware is actually designed to be foolproof. You can short any pin to any other pin and guarantee no damage. It's also difficult to break with external sources. You can hook up 18V directly to the signal generator, for example, and the only thing that will burn is one of "fuse" resistors which can be easily replaced with a blob of solder. Even if you can't solder, only the one output you damaged will become faulty; the rest will work OK.
> 
> Not really sure what I could do to make the software easier to use, but open to suggestions (please create a separate issue though)!

I am thinking of something like
* Vernier Logger Pro: https://www.vernier.com/products/software/lp/
* Vernier DataQuest™ Software for TI-Nspire™: https://www.vernier.com/platforms/texas-instruments/software/data-collection/dataquest/

Basically both have a play/stop button to start/stop capturing of data. The data is shown in a table (time series) and in an plot. Additionally the software has a database for sensors available to be able to have the correct ranges, units, etc. ready. This database could be something simple like an ini file.

> Send me an email at admin@espotek.com and I can get you a good deal on a class set, especially if you're happy to share educational materials you make. :)

This is the direction I am thinking of. ;))

**Comment by EspoTek** [comment]
Hey, sorry about the late response.  Have just been ridiculously overwhelmed at work.

The software idea looks pretty cool, but I don't have the time to develop it myself right now.  There's an API that just needs a bit of polishing up before release, though, and that could be used to make software like this.  Are you any good at programming?

Cheers,
~Chris

**Comment by drtrigon** [comment]
> Are you any good at programming?

I can solve issues by programming (python, c/c++) - but I would not talk about "how good I am"... ;) Would it be possible to release the API - even if it is not polished yet?

**Comment by EspoTek** [comment]
Of course.  It's been part of the main tree for a while.
https://github.com/EspoTek/Labrador/tree/master/Librador_API

Note that it's Linux-only for the moment.

**Comment by EspoTek** [comment]
Oh, and here's a full user guide.  
https://docs.google.com/document/d/11Cu6602X_y5x0IwIBZnP7ImIx0jykX7AzToh83-7hCM/edit?usp=sharing

It's basically public-beta ready.

**Comment by drtrigon** [comment]
Cool! Thanks a lot! Greetings

**Comment by EspoTek** [comment]
^^ Wow, that is a lot of ICs for a fairly similar device to the Labrador.  I think I've got two chips with more than 3 pins?

**Comment by drtrigon** [comment]
So let's do it better ... correct?

**Comment by EspoTek** [comment]
You mean a higher end Labrador 2.0?  If only I had the time!

**Comment by drtrigon** [comment]
Let's start and do it step-by-step. What's the first point? Specs and search for key parts?


Am 10. Februar 2019 00:39:33 MEZ schrieb Chris Esposito <notifications@github.com>:

**Comment by EspoTek** [comment]
Yep, that's the first step.  Important features are a High-speed USB 2.0 transceiver (not full-speed, which is annoying 1/40th the speed of high speed!), fast ADC, DMA and good documentation/support.
I remember reading about a MCU that had all of these features, but it cost around $7 per IC (compared to $2 for the Labrador 1.0's XMEGA32A4U).
Once I've picked a part I'd need to make sure that the software is basically plausible.
Next step would be to redesign the analog front-end.  6 resistors and half an LM324 won't cut it for higher frequency/bandwidth.  Finally, all of the software - both embedded and fixing the desktop software to get it to work with the new hardware.

Completely doable, but would be a massive investment of time which I would honestly rather put towards marketing Labrador 1.0 - at least for 2019.
It's a great product, but I only sell a few of them a week.  I think a big part of that is because I'm not getting out there and letting people know that it exists.  Both times it was reviewed in a magazine I sold 30-40 in the space of 2 weeks, and that was before the site redesign and eBay/Amazon listings (I was selling maybe 2-3 a week then, compared to 4-5 now).  More marketing materials (e.g. a demonstration video on the website) and some tutorials/educational materials would help a lot too.  \
At the end of the day, I'd honestly rather have 10,000 users with Labrador 1.0 than 2,000 users with Labrador 1.0 and another 2,000 users with Labrador 2.0.  Both in terms of business, and in terms of making a difference in electronics education, the more people that have access to hardware, the better.

**Comment by drtrigon** [comment]
Thanks for the insight!

> More marketing materials (e.g. a demonstration video on the website) and some tutorials/educational materials would help a lot too. 

Exactly what came to my mind... I am Physicist so let's brainstorm about that. With Labrador only, you can do power consumption measurement of e.g. a phone, a quadcopter, ... else?
For education or school some additional sensors might be needed.

Currently I work in a technical highscool that started a new program 3 years ago. My boss did and still does at least 1 visit for promo a week (for 3 years now). I also do some, why not for Labrador also? Good thing here in Switzerland the Labrador cost about the price of 3-4 boxes of cigarettes - so it's really affordable.

**Comment by ajxn** [comment]
My 2nd year Computer Engineering students have a project that could be to
design a prototype for a GUI in Java or something like that.
To bad it is in the winter, so that project course has already passed. Next
time maybe?
 If I don't contact you about that in september, you are welcome to contact
me to see what we can do. :-)

Den ons 13 feb. 2019 kl 23:15 skrev Chris Esposito <notifications@github.com
>:

> Yep, that's the first step. Important features are a High-speed USB 2.0
> transceiver (not full-speed, which is annoying 1/40th the speed of high
> speed!), fast ADC, DMA and good documentation/support.
> I remember reading about a MCU that had all of these features, but it cost
> around $7 per IC (compared to $2 for the Labrador 1.0's XMEGA32A4U).
> Once I've picked a part I'd need to make sure that the software is
> basically plausible.
> Next step would be to redesign the analog front-end. 6 resistors and half
> an LM324 won't cut it for higher frequency/bandwidth. Finally, all of the
> software - both embedded and fixing the desktop software to get it to work
> with the new hardware.
>
Wouldn't an embedded ARM M0 CPU be good for a more high end Labrador 2.0?
They are also popular in Maker space, like the ATXMEGA32 is. There are
great small embedded chips which would fit your description. Might have a
look at USB 3 for higher speed transfer, if possible in the cost frame.
Faster and more memory then the ATXMEGA32A4U 8-bit chip.
That is, something like ARM M0 core at 48MHz with DMA, 12 bit ADC and USB
and a nice price of about €1.16 for 100:
https://www.mouser.se/datasheet/2/389/stm32f070c6-956182.pdf

Might even show up as a USB memory stick where it simulated files that can
be used to read samples from, and write commands to configure the
Labrador.  Might make the software for hosts a bit easier to write?
The firmware for Microbit uses that approach to download and reprogram it,
open source that is.

Oh, so much fun project and so little time. :-)

> Completely doable, but would be a massive investment of time which I would
> honestly rather put towards marketing Labrador 1.0 - at least for 2019.
> It's a great product, but I only sell a few of them a week. I think a big
> part of that is because I'm not getting out there and letting people know
> that it exists. Both times it was reviewed in a magazine I sold 30-40 in
> the space of 2 weeks, and that was before the site redesign and eBay/Amazon
> listings (I was selling maybe 2-3 a week then, compared to 4-5 now). More
> marketing materials (e.g. a demonstration video on the website) and some
> tutorials/educational materials would help a lot too.
> At the end of the day, I'd honestly rather have 10,000 users with Labrador
> 1.0 than 2,000 users with Labrador 1.0 and another 2,000 users with
> Labrador 2.0. Both in terms of business, and in terms of making a
> difference in electronics education, the more people that have access to
> hardware, the better.
>
Know nothing abut marketing, sorry.  :-)

And yes, please ignore as I am just armchair coding here. But would be nice
to hear about what you might think about those thoughts. You that actually
have done the work with Labrador.

/Jackson

**Comment by EspoTek** [comment]
> Exactly what came to my mind... I am Physicist so let's brainstorm about that. With Labrador only, you can do power consumption measurement of e.g. a phone, a quadcopter, ... else?
> For education or school some additional sensors might be needed.

Yeah, agreed.  Labrador on its own is not super exciting.  An experiments book that you can use with a cheaply available, common kit from AliExpress/eBay (or perhaps even my own home-made kit, if I were to be a better businessman) would really drive home the educational possibilities of Labrador, and perhaps something that you eventually build up into a 3D printed robot would be even cooler.  You could really show off the advantages of having a scope there, with AC measurements on the power supply rails before/after R/L filtering, direct reads on sensors so people can actually understand what the code is doing and more.  Again, though, this all takes time.  Perhaps I should talk to my employer about working 4 days a week.  Not being entirely un-serious there.

> Currently I work in a technical highscool that started a new program 3 years ago. My boss did and still does at least 1 visit for promo a week (for 3 years now). I also do some, why not for Labrador also? Good thing here in Switzerland the Labrador cost about the price of 3-4 boxes of cigarettes - so it's really affordable.

Not quite sure what you mean here?  As in visit the high school and try to sell the Labrador to students?  Or teachers?  I've sold some boards at a group of guys who do Microcontroller stuff once, and that went pretty well (about 20 in one night, can't complain), but I'm just not quite sure how to break into education without first developing at least some basic teaching aids.

**Comment by drtrigon** [comment]
> Perhaps I should talk to my employer about working 4 days a week. Not being entirely un-serious there.

As I am studying (still!) and because of family, I am working 3 days per week only.

> Not quite sure what you mean here? As in visit the high school and try to sell the Labrador to students? Or teachers? I've sold some boards at a group of guys who do Microcontroller stuff once, and that went pretty well (about 20 in one night, can't complain), but I'm just not quite sure how to break into education without first developing at least some basic teaching aids.

Schools, Students and Teachers are good customers for sure, but I thought more general e.g. fab labs, maker spaces but also enthusiasts and public in general. My focus is on the promo, you have to go out there in order to reach the people. As often as possible, e.g. once a week.

**Comment by EspoTek** [comment]
> My 2nd year Computer Engineering students have a project that could be to design a prototype for a GUI in Java or something like that. To bad it is in the winter, so that project course has already passed. Next time maybe? If I don't contact you about that in september, you are welcome to contact me to see what we can do. :-)
Oh, that would be grest.  Please send me an email at admin@espotek.com so I can contact you about it in September (unless you don't mind posting your email on a public forum!)

> Wouldn't an embedded ARM M0 CPU be good for a more high end Labrador 2.0? They are also popular in Maker space, like the ATXMEGA32 is. There are great small embedded chips which would fit your description. Might have a look at USB 3 for higher speed transfer, if possible in the cost frame. Faster and more memory then the ATXMEGA32A4U 8-bit chip. That is, something like ARM M0 core at 48MHz with DMA, 12 bit ADC and USB and a nice price of about €1.16 for 100: https://www.mouser.se/datasheet/2/389/stm32f070c6-956182.pdf Might even show up as a USB memory stick where it simulated files that can be used to read samples from, and write commands to configure the Labrador. Might make the software for hosts a bit easier to write? The firmware for Microbit uses that approach to download and reprogram it, open source that is. Oh, so much fun project and so little time. :-)

Actually, the CPU and RAM don't matter much for Labrador - almost all of the actual processing is done on the user's PC and that's easily 100x the FLOPpage (technical term) of a 32-bit ARM Cortex M0.  Actually, if you look at the code for the XMEGA, the CPU does nothing apart from initialise the hardware and events system, acknowledge USB commands and calibrate the clock.  Everything is driven by the events system and DMA, so the most important specs are ADC sample rate and DMA throughput.  CPU-independent triggering is a necessity too.

I've looked at the STM32 series before and they are almost perfect for my purposes.  The F3 series can have up to 4 ADCs at 5Msps each (ie 20Msps total), but you cannot add USB 2.0 high-speed to it.  The F2 and F4 series allow you to add USB 2.0 High-speed PHYs, but the ADC only samples at 2Msps.  Both have plenty of DMA bandwidth, as well as built-in opamps and a 2-channel DAC.  Price is low too.  If only the F3 did USB HS!!!

Not quite sure how I'd work with files as the samples need to come in as a continuously updated stream.  At the moment, it uses a double ring buffer to store everything but to work with files I'd need to continuously update and stomp older files.  It does actually make sense to use HDD or SSD to increase the size of the buffer above and beyond the users' RAM though, and I could even add this to Labrador 1.0! 

> Know nothing abut marketing, sorry. :-) And yes, please ignore as I am just armchair coding here. But would be nice to hear about what you might think about those thoughts. You that actually have done the work with Labrador. /Jackson
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

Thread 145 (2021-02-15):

### ISSUE TITLE
Device not connected and other issues

### ISSUE THREAD

**Issue by hchaudh2** [EspoTek/Labrador#145]
I have tried to download Mac OS Continuous Build from this link: https://github.com/EspoTek/Labrador/releases
however, I am unable to open Labrador application. So I downloaded Mac OSX from this link https://github.com/EspoTek/Labrador/releases/tag/1.1  and it opens however when I try plugging in usb to calibrate, it says device not connected. I have even tried firmware recovery and multiple USB cables especially those that support data transfer. I'm using an adapter so I only have one USB port on it so one device is connected at a time. But even then it says device is not connected. I'm using this for an electric circuits class in college and have a deadline for a lab report. So, can you help me out please? What is the issue here?

**Comment by EspoTek** [comment]
Can you please give me the output of `lsusb` when the board is connected?

You can install it and run it through Homebrew:
```
/bin/bash -c "$(curl -fsSL https://raw.githubusercontent.com/Homebrew/install/HEAD/install.sh)"
brew install lsusb
lsusb
```

**Comment by hchaudh2** [comment]
I had already downloaded Homebrew earlier today. But this is what I got when I connected the board. 

>huriyyah@Huriyyahs-MacBook-Pro-2 ~ % lsusb
2021-02-13 00:12:00.434 system_profiler[10794:200635] SPUSBDevice: IOCreatePlugInInterfaceForService failed 0xe00002be
2021-02-13 00:12:00.434 system_profiler[10794:200635] SPUSBDevice: IOCreatePlugInInterfaceForService failed 0xe00002be
2021-02-13 00:12:00.435 system_profiler[10794:200635] SPUSBDevice: IOCreatePlugInInterfaceForService failed 0xe00002be
2021-02-13 00:12:00.435 system_profiler[10794:200635] SPUSBDevice: IOCreatePlugInInterfaceForService failed 0xe00002be
2021-02-13 00:12:00.436 system_profiler[10794:200635] SPUSBDevice: IOCreatePlugInInterfaceForService failed 0xe00002be
2021-02-13 00:12:00.436 system_profiler[10794:200635] SPUSBDevice: IOCreatePlugInInterfaceForService failed 0xe00002be
2021-02-13 00:12:00.436 system_profiler[10794:200635] SPUSBDevice: IOCreatePlugInInterfaceForService failed 0xe00002be
Bus 000 Device 001: ID 05ac:1018 Apple Inc. USB3.1 Hub  Serial: DLC01230154KD56A2
Bus 020 Device 001: ID 05ac:1017 Apple Inc. USB2.0 Hub  Serial: DLC01230154KD56A2
Bus 020 Device 003: ID 03eb:a000 Atmel Corporation USBGobindar Dummy Device 
Bus 020 Device 002: ID 05ac:1463 Apple Inc. USB-C Digital AV Multiport Adapter  Serial: DLC01230154KD56A2
Bus 128 Device 000: ID 05ac:8102 Apple Inc. Touch Bar Backlight  Serial: 0000000000000000
Bus 128 Device 000: ID 05ac:8302 Apple Inc. Touch Bar Display  Serial: 0000000000000000
Bus 128 Device 000: ID 05ac:027f Apple Inc. Apple Internal Keyboard / Trackpad  Serial: FM702860219N1R1A2+RWN
Bus 128 Device 000: ID 05ac:8103 Apple Inc. Headset  Serial: 000000000000
Bus 128 Device 000: ID 05ac:8262 Apple Inc. Ambient Light Sensor  Serial: 000000000000
Bus 128 Device 000: ID 05ac:8514 Apple Inc. FaceTime HD Camera (Built-in)  Serial: CC20272G4LHJ3Y328
Bus 128 Device 000: ID 05ac:8233 Apple Inc. Apple T2 Controller  Serial: 0000000000000000
Bus 000 Device 001: ID 1d6b:CITR Linux Foundation USB 3.1 Bus 
Bus 000 Device 001: ID 1d6b:0003 Linux Foundation 3.0 root hub 
Bus 000 Device 000: ID 05ac:8102 Apple Inc. Apple T2 Bus 
huriyyah@Huriyyahs-MacBook-Pro-2 ~ %

**Comment by hchaudh2** [comment]
I had already downloaded Homebrew earlier today. But this is what I got when I connected the board.

2021-02-13 00:12:00.434 system_profiler[10794:200635] SPUSBDevice: IOCreatePlugInInterfaceForService failed 0xe00002be
2021-02-13 00:12:00.434 system_profiler[10794:200635] SPUSBDevice: IOCreatePlugInInterfaceForService failed 0xe00002be
2021-02-13 00:12:00.435 system_profiler[10794:200635] SPUSBDevice: IOCreatePlugInInterfaceForService failed 0xe00002be
2021-02-13 00:12:00.435 system_profiler[10794:200635] SPUSBDevice: IOCreatePlugInInterfaceForService failed 0xe00002be
2021-02-13 00:12:00.436 system_profiler[10794:200635] SPUSBDevice: IOCreatePlugInInterfaceForService failed 0xe00002be
2021-02-13 00:12:00.436 system_profiler[10794:200635] SPUSBDevice: IOCreatePlugInInterfaceForService failed 0xe00002be
2021-02-13 00:12:00.436 system_profiler[10794:200635] SPUSBDevice: IOCreatePlugInInterfaceForService failed 0xe00002be
Bus 000 Device 001: ID 05ac:1018 Apple Inc. USB3.1 Hub Serial: DLC01230154KD56A2
Bus 020 Device 001: ID 05ac:1017 Apple Inc. USB2.0 Hub Serial: DLC01230154KD56A2
Bus 020 Device 003: ID 03eb:a000 Atmel Corporation USBGobindar Dummy Device
Bus 020 Device 002: ID 05ac:1463 Apple Inc. USB-C Digital AV Multiport Adapter Serial: DLC01230154KD56A2
Bus 128 Device 000: ID 05ac:8102 Apple Inc. Touch Bar Backlight Serial: 0000000000000000
Bus 128 Device 000: ID 05ac:8302 Apple Inc. Touch Bar Display Serial: 0000000000000000
Bus 128 Device 000: ID 05ac:027f Apple Inc. Apple Internal Keyboard / Trackpad Serial: FM702860219N1R1A2+RWN
Bus 128 Device 000: ID 05ac:8103 Apple Inc. Headset Serial: 000000000000
Bus 128 Device 000: ID 05ac:8262 Apple Inc. Ambient Light Sensor Serial: 000000000000
Bus 128 Device 000: ID 05ac:8514 Apple Inc. FaceTime HD Camera (Built-in) Serial: CC20272G4LHJ3Y328
Bus 128 Device 000: ID 05ac:8233 Apple Inc. Apple T2 Controller Serial: 0000000000000000
Bus 000 Device 001: ID 1d6b:CITR Linux Foundation USB 3.1 Bus
Bus 000 Device 001: ID 1d6b:0003 Linux Foundation 3.0 root hub
Bus 000 Device 000: ID 05ac:8102 Apple Inc. Apple T2 Bus

**Comment by EspoTek** [comment]
I see the issue now: it enumerates as `Bus 020 Device 003: ID 03eb:a000 Atmel Corporation USBGobindar Dummy Device`.
There was a firmware issue with one particular batch of the boards produced last year, as well as a hotfix for this firmware issue in the newest version of the desktop software.

If you're able to connect your board to another PC running the latest version of the desktop software, the firmware will be fixed on your board and the board will connect in future.  If you don't have another PC, a VM should work too.

**Comment by hchaudh2** [comment]
It worked! Thank you for that! Also what should I do if my multimeter in labrador is not working. I'm unable to click on anything like for example: I'm trying to change the mode to I, but I cannot do that.

**Comment by hchaudh2** [comment]
It worked! Thank you for that!

**Comment by EspoTek** [comment]
Good to hear, and sorry about the runaround.
Regarding the multimeter issue, read "A Note on Buffers" here:
https://github.com/EspoTek/Labrador/wiki

You'll need to turn off the oscilloscope before you can turn on the multimeter.

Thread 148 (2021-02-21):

### ISSUE TITLE
Scope reads 4.5Vdc but multimeter reads 3Vdc

### ISSUE THREAD

**Issue by macktion** [EspoTek/Labrador#148]
Hi. I'm monitoring a small 4.5Vdc 1A PSU used on some tiny Christmas lights.  The Labrador zoomed-in shows quite smooth 4.5 (0v offset)but the multimeter shows only approx 3.15V max/min/RMS.  shouldn't the scope and meter values be close?  

I also haven't had luck measuring current with the Lab. trying to verify/improve the accuracy of the 200Ma I measured with my discrete meter that created a significant/unwanted series load that dims the lights. I could not even get the Lab to allow the string of lights to turn on while indicating current as high as 1.5A at 0ohms series.

**Comment by EspoTek** [comment]
The multimeter measures the difference between CH1 and CH2.  If nothing is attached to CH2, it'll float towards VCC/2 (around 1.65V).
Please see documentation here:
https://github.com/EspoTek/Labrador/wiki

Current measurements with a low burden voltage is not a standard feature of most multimeters, including Flukes.
It's possible to use an external amplifier circuit to lower burden voltage to near-zero, though.
Dave Jones did a video on it a while back:
https://www.youtube.com/watch?v=jx0dryLmUEQ

**Comment by macktion** [comment]
Thank you.  Very helpful.

**Comment by lkoepsel** [comment]
This issue is happening for me. If one follows the following process, it is easy to replicate.
1. Open Labrador application, press M to bring up Range Dialog and change Vmax to 5V.
2. Connect Oscilloscope CH1 to Power Supply (Positive) and Oscilloscope CH2 to Power Supply (GND) *Note the CH1 line is about 4.8V and is solid, no noise.*

![Screen Shot 2021-03-27 at 7 38 46 AM](https://user-images.githubusercontent.com/7906684/112724224-8f63f800-8ecf-11eb-872b-a5502aad5934.png)

3. Uncheck Oscilloscope CH1 and check Multimeter, all of the values (Max, Min, Mean and RMS) will be identical and incorrect. In this case, 2.96V. *Note CH1 line has now moved to 2.96V, continues to be solid, no noise*

![Screen Shot 2021-03-27 at 7 34 55 AM](https://user-images.githubusercontent.com/7906684/112724269-c934fe80-8ecf-11eb-886f-a8ab03d95912.png)

4. Uncheck Multimeter and check Oscilloscope then check Paused and uncheck Paused. *Note the CH1 line moves up to 4.9V and once Paused is unchecked, the line appears with a slight amount of noise*
5. Uncheck Oscilloscope and check Multimeter and the values:
     * Are correct when compared with a DMM
     * Are not all identical, they vary with a little bit of noise.
 
![Screen Shot 2021-03-27 at 7 35 25 AM](https://user-images.githubusercontent.com/7906684/112724181-41e78b00-8ecf-11eb-9975-4d2970f861f6.png)

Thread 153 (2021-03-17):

### ISSUE TITLE
How to Connect Labrador to Computer

### ISSUE THREAD

**Issue by ddd15dd** [EspoTek/Labrador#153]
Hi, I am using a USB to microUSB cord to connect the labrador to my laptop, and the Red LED light lights up. But when I open the software it says Device Not Connected. For my circuits lab, it says that I should calibrate it before plugging the Labrador into the breadboard. But when I try to do that I get an error message "You need to connect the board before calibrating it!"

Please help!

**Comment by EspoTek** [comment]
Please see the troubleshooting guide here:
https://github.com/EspoTek/Labrador/wiki/Troubleshooting-Guide

The most common issue I hear about is caused by people using a USB cable without data lines.  When you use that same cable to connect a USB device (such as an Android phone) to your computer, is that device detected?

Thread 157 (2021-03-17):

### ISSUE TITLE
help measuring current in multimeter mode

### ISSUE THREAD

**Issue by khtodd1** [EspoTek/Labrador#157]
Hello.  I'm trying to use Labrador to measure the gate current when switching on a MOSFET from an output of a microcontroller.  I've read the Wiki 500 times but I'm not still not quite sure how to connect it to measure what I want.  Can you please explain, or even better, throw up a quick circuit sketch?  Thank you.

**Comment by EspoTek** [comment]
Unfortunately, I don't think it's a simple task for a device such as this to measure MOSFET gate currents as they're likely to be in the nA range.
However, if you could, the circuit diagram would like like this:
![IMG_8859](https://user-images.githubusercontent.com/22040436/111422374-b3427380-8742-11eb-9471-5c4e0f4ebf88.JPG)
A load resistor is placed in series with the current you want to measure, and the two channels of the scope are added across the load.

The software interface looks like this:
<img width="770" alt="Untitled" src="https://user-images.githubusercontent.com/22040436/111422443-d3723280-8742-11eb-9d94-0e8e1c83b8df.png">
Set the multimeter mode to "I" and manually enter the value of the series resistance (load resistor from circuit diagram) into the box shown.

Sorry if I can't be of more help.  If you're really keen to measure something that small, maybe consider looking to the uCurrent or similar?

**Comment by khtodd1** [comment]
Thank you for your help with this - it's a power MOSFET - so the gate
current could actually get up to 100mA or so, although I'd like to see it
on the order of 10-15mA.  I will try your suggestion.

**Comment by EspoTek** [comment]
Ahh, of course.  You should have no issue then.

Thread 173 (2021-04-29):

### ISSUE TITLE
External Scope probes?

### ISSUE THREAD

**Issue by kevinpowell** [EspoTek/Labrador#173]
Breadboard mounting is fine, but I'm more likely to put the Labrador in a small enclosure and wire up a couple bnc connectors for a traditional scope probe.  Would there be any issues doing this?  Will a standard tektronix (1x and 10x) probe work well?

**Comment by EspoTek** [comment]
Hi Kevin, you'll have absolutely no issues with this.  It's quite common for people to do this, and there are even 3D printable enclosures on Thingiverse with holes for BNC probes.

Good luck with the projects, and feel free to send pics when you're done.  Always like seeing what people get up to!

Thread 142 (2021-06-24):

### ISSUE TITLE
"Calibrate on connection" calibrates on all reconnections.

### ISSUE THREAD

**Issue by maith1** [EspoTek/Labrador#142]
We are using the Labrador for a class electric circuits lab. Our instructions were to create a simple circuit on a breadboard with two wires and a resistor. After doing this, the Labrador shuts off and then wants to recalibrate again. This basically forces me into an infinite loop of recalibration. Is my Labrador broken or could I be doing something wrong?

**Comment by EspoTek** [comment]
Which OS are you using?  The calibration routine is completely managed by the PC and has nothing to do with the hardware.

**Comment by maith1** [comment]
I am using Windows 10. The calibration seems to go just fine before I plug anything in but once I form a full circuit, the red light on the device shuts off. When I unplug it and plug it back in, it wants to calibrate again.

**Comment by EspoTek** [comment]
OK, so it looks like there's two independent issues here.
The first issue is a minor software bug - it seems that asking it to calibrate when the board is connected (on initial launch) will ask it to calibrate _every_ time the board is connected.  Relaunching the software will fix this.

The second issue is most likely caused by an short somewhere in your circuit.  Please check it very, very carefully, and make sure you're aware how the breadboard is laid out.

**Comment by maith1** [comment]
I have installed the software on another computer entirely and am still encountering the same problem. My circuit appears to be constructed more or less the same as the one our lab tutorial shows as well. I'm not sure what could be causing this other than maybe a faulty Labrador?

**Comment by EspoTek** [comment]
If the light turns off, it means the OCP is tripping.  Either the factory installed a bad fuse (which can be routed around), or there is an issue with the circuit.  Please send me some pics of your attached circuit and I can map out where the short is for you.

**Comment by maith1** [comment]
![File_000](https://user-images.githubusercontent.com/5343409/107583674-411dc280-6bc9-11eb-8f57-63acefc4bde6.jpeg)
I am relatively new to doing this kind of stuff so it is highly likely that I am doing something incorrectly. I just set this up the way that my lab instructions appeared to show. I'm sorry if the problem is obvious and I'm missing it.

**Comment by EspoTek** [comment]
OK, I can see what's going on here.
Honestly, the problem is obvious to a trained engineer but everyone (myself included) makes this exact kind of error when starting out.

Check out the chart here:
https://www.electronics-tutorials.ws/resistor/res_2.html

The questions to ask yourself are the following:
 - What is the resistance value of the resistor?
 - How much current is it drawing?
 - How much power is being dissipated by it?
 - How does this value compare to the max power that Labrador can supply?

(Obviously it's a leading question, but I recommend doing the maths anyway.  The magnitude differences are pretty impressive!)

**Comment by maith1** [comment]
Thank you for the helpful information. I will try to work this out now that I know where to start. I believe now that I can close this ticket. Thank you once again! Sorry for the inconvenience.

**Comment by EspoTek** [comment]
I think it's best to leave the ticket open.  While the disconnect wasn't a bug in Labrador, the re-calibration over and over again definitely was!

**Comment by maith1** [comment]
Okay! I'm not too familiar with the GitHub ticket system so I'm not really sure of the implications of opening and closing tickets but if you believe it should stay open then I trust your judgment. If I have any more problems then I guess I'll put them here. Thanks again.

**Comment by EspoTek** [comment]
Abandoning this issue.  It's low priority and honestly a mess of a system to fix.

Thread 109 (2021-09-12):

### ISSUE TITLE
flashing device firmware locks up

### ISSUE THREAD

**Issue by perigalacticon** [EspoTek/Labrador#109]
Upon installation of latest interface program on windows 10 pc, and connecting the scope, the program reports "flashing device firmware" but it gets stuck here for at least 15 minutes and appears to be locked up.

**Comment by EspoTek** [comment]
I just downloaded the latest version on my machine and plugged in a board with older firmware.  The firmware flash completed in a couple of seconds.

I suspect something else may have changed on your system, or something has happened to the board.
Please restart your PC, and then try the "Firmware Recovery" option from the "Help" menu of Labrador.

**Comment by perigalacticon** [comment]
Thanks.  Here's exactly what happens.  If I plug in the board before starting the program a notification window pops up asking for calibration.  It doesn't matter what I choose, the program then fails to start.  When launch it again (from my desktop) it asks to calibrate, again my choice doesn't affect the result but then it starts and shows device not connected.  If I then re-plugin the board it goes to flashing device firmware, and nothing I do changes that message and the scope does not run but the controls seem to react very slowly as if it is bogged down doing something.  

If I launch the program before connecting it still asks to calibrate, again my choice does not affect it and the only difference is the program launches the first time.  

I tried the firmware recovery help option, it says it appears to be configured so the problem could be the USB set up.  So I plugged the USB into various USB ports, including a USB hub I have that has the blue USB ports mentioned.  Nothing has changed the behavior of the launch process I described.

**Comment by EspoTek** [comment]
Odd.  Did it used to work in an older version of the software?

Under `C:\Program Files\EspoTek\EspoTek Labrador\firmware` you should see a batch file called "flash.bat".  If you set the board to bootloader mode (see https://github.com/EspoTek/Labrador/wiki) and then run that batch file, does it fix things?

**Comment by phr0gger** [comment]
I have seen Labrador showing a (bogus?!) Flashing Firmware message on the Raspberry Pi 3B+. 
It happens when restarting the Labrador software (but not unplugging the board) after there were -9 errors (unixUsbDriver::usbSendControl FAILED with error LIBUSB_ERROR_PIPE). The board supposedly reports FIRMWARE VARIANT = 0x00 and the software attempts to flash the board. However, the USB driver is still not working and nothing happens. One needs to power cycle the board to re-initialize the USB driver.

**Comment by 99Phish** [comment]
Terribly sorry for resurrecting an old thread.


Im afraid I am in the same boat as op.  I have the software running on my windows work pc, Albeit an older version. I also have it running on macOS after the recent continuous build update (the one after 9/2/21).

I am now just installing the software fresh on my personal pc only to encounter "flashing device firmware" without resolution..

This board has saved my hide in the field more than once so I am not complaining.  I just thought I should document the problem. I also tried plugging in the board before and after I start the software. All to the same effect. 

On my work pc and my work macbook, sometimes I need to unplug and replug the usb cable to get the software to recognize the controller on boot up.  After a single power cycle it always gets recognized and hums along as well as expected.

I seem to be running into a driver problem based off of device manager. The first image "flashing" is what I encountered after plugging in the device.

The second image "reinstalled" is what I encountered after reinstalling the current windows build. 

 ![reinstalled](https://user-images.githubusercontent.com/39873285/132972990-94053a41-b80f-4950-af38-69e0be5b9d10.png)

![Flashing](https://user-images.githubusercontent.com/39873285/132972874-6bacc04f-c2c1-47b3-b024-cdd13b706a1a.png)

--later on--

I happen to have my macbook pro with me and  connecting the labrador to that computer also results in failure. This time I am being prompted to connect the device.  

The problem is likely on my end all things considered.  I typically keep the board in my backpack in the original packaging. Pink foam and the esd bag.

**Comment by EspoTek** [comment]
Hi mate, that's very bizarre.  I suspect it's a hardware fault, but it could also possibly be a bad flash.

The first thing I'd do is to see if the board enumerates correctly when in bootloader mode.
To do this, connect Digital Out 1 to GND then reconnect your board:
https://github.com/EspoTek/Labrador/wiki/Pinout

You should see an "Atmel ATXMega32A4U" device in Device Manager if the bootloader is good.

If that works, you can go to C:/Program Files/EspoTek/EspoTek Labrador/Firmware and run the files "wipe.bat" then "flash.bat".  They should take a couple of seconds each to run (if the window immediately closes, that's not good) and the board should be back to normal.

If that doesn't work, I'd recommend trying a different cable.  If it's not the cable, contact me at admin@espotek.com and we can look into getting a replacement sent to you.

Cheers,
~Chris

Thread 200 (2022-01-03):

### ISSUE TITLE
Raspberry Pi 4b - "Calibration has been abandoned due to out-of-range values"

### ISSUE THREAD

**Issue by fluxsauce** [EspoTek/Labrador#200]
Good news - I can calibrate with Windows 10 without issue! I'm assuming the unit itself is fine.

Difficulty - I can't get it to calibrate on a Raspberry Pi 4b, Raspberry Pi OS with desktop 5.10.

The device detects and connects. The software seems to be working correctly, other than this calibration step?

I had to struggle a bit to get it installed, https://github.com/EspoTek/Labrador/issues/197 mentions it and the workaround is what I did (honestly, after Googling first, then I found the issue 😆)

Raspberry Pi firmware is current, upgraded as part of this process. I also used a breadboard to ground it, same effect, so it's not an intermittent connection. I'm using a dedicated USB-C power supply (Canakit) connected to a nicely grounded circuit so I'm assuming that's not it either.

Steps to reproduce:

![PXL_20211220_010136172 MP](https://user-images.githubusercontent.com/976391/146698317-ad3d31f9-0da7-4d26-8b80-abeef87d0f3c.jpg)
![PXL_20211220_010142160](https://user-images.githubusercontent.com/976391/146698318-557fea84-4f7d-4344-a903-a7d1c488ac80.jpg)
![PXL_20211220_010153736](https://user-images.githubusercontent.com/976391/146698319-289a9002-7d64-4a40-aeea-419e9d3b1b7e.jpg)
![PXL_20211220_010203852 MP](https://user-images.githubusercontent.com/976391/146698320-de449f95-fc31-4c02-a44d-e460925bfa7f.jpg)
![PXL_20211220_010226382](https://user-images.githubusercontent.com/976391/146698321-af50dfb1-26a8-4da4-a8a9-c59843c82005.jpg)
![PXL_20211220_010230658](https://user-images.githubusercontent.com/976391/146698323-77ddf824-34c0-4aa5-9f2b-2023c032c6b0.jpg)
![PXL_20211220_010240404](https://user-images.githubusercontent.com/976391/146698324-5f02b04e-298d-48ad-bd4d-f0f75da27fab.jpg)

With debug:

```
DEBUG MODE ACTIVE
unified debug is of size 27
...
Changing workspace...
Calibration routine beginning!
unified debug is of size 27
...
VRef (CH1) =  1.50071
VRef (CH2) =  1.4656
unified debug is of size 27
...
unified debug is of size 27
VMeasured (CH1) =  0.379172
VMeasured (CH2) =  0.369023
...
```

Thanks!

**Comment by EspoTek** [comment]
Any idea what those big bursts of noise are on the trace in pics 1 and 2?

**Comment by fluxsauce** [comment]
Breadboard jumpers were connected to the Labrador.

Nothing connected except USB cable:

https://user-images.githubusercontent.com/976391/146708428-9f58b94f-8845-4714-9db5-1380510ebee9.mp4

**Comment by EspoTek** [comment]
OK, that makes more sense.  Looking at the log, it seems like it detected a higher value than expected in the second stage.  Perhaps you lost contact temporarily, just before pressing OK?

**Comment by lchen198** [comment]
I am having the same issue on raspberry pi 4 and tried multiple times without luck.  It works fine on Win 11.

...
genericUsbDriver dectructor entering
genericUsbDriver dectructor completed
Reinitialising USB driver!
Making USB Driver invisible!!
pipeID 0 = 129
Generic Usb Driver setup complete
unixUsbDriver created!
ReinitUsbStage2 is returning
deviceConnectedDisplay::connectedStatusChanged running!
CHECKING CONNECTION!
Entering unixUsbDriver::usbInit
Libusb context initialised
Device found!!
KERNEL DRIVER INACTIVE
Interface claimed!
Connected
BOARD IS RUNNING FIRMWARE VERSION 0x0006
EXPECTING FIRMWARE VERSION 0x0006
FIRMWARE VARIANT = 0x02
EXPECTED VARIANT = 0x02
Connecting now!
deviceConnectedDisplay::connectedStatusChanged running!

...

unified debug is of size 27
unified debug is of size 27
unified debug is of size 27
VMeasured (CH1) =  0.466232
VMeasured (CH2) =  0.467766
unified debug is of size 27
unified debug is of size 27
unified debug is of size 27

**Comment by StriderTR** [comment]
I'm having the same issue, mine seems to read a constant 1.6V, but fails at the grounding. I tried grounding several ways, even to my PC's PSU.

I am also using mine with a Pi 4, same setup as the OP. My Pi 4 is in a Argon M.2 case. If I figure it out, I'll post it. :)

**Comment by theblaz** [comment]
Having the same issues but with the Linux AppImage on an x86 computer. Could there be an issue with the Linux reading values? Calibration works from windows application

**Comment by EspoTek** [comment]
I've had several reports of this bug across all platforms, and can't for the life of me reproduce it on any of my systems at home.  It seemed to appear about 2-3 months ago, and can disappear randomly too.  I'm not sure what the source of this could be, but it might be best to just roll back some patches from the past few months.

**Comment by theblaz** [comment]
thanks for the update. I'll keep playing with it.

**Comment by lchen198** [comment]
Maybe try a different USB cable?  I haven't tried it yet but I wonder if connecting the ground pin on the board with raspberry pi ground pin would help.

**Comment by theblaz** [comment]
I tried several different cables and different ports as well as different
machines. The consistency seems to be Linux as I am able to get it to work
in windows. I haven't tried it on a Mac yet.

**Comment by StriderTR** [comment]
Nice to see it's not just me. 

I tried 4 different USB cables as well as different grounding methods. I  have not tried on my Windows machine yet, haven't had time. 

I can say that the "noise" you see in the OP, I see as well, I just assumed it was when my skin touched the wires. That's what led me to try different grounding methods, I was assuming it was seeing static through those thin jumper wires. Still, same problem.

**Comment by EspoTek** [comment]
The noise is a separate issue, and not something I've seen outside of the Pi (again, not critical and not something I'm able to reproduce with my Pi 3, so I haven't spent too much time looking into it)!

The common thing that people seem to be is the trace freezing after a few seconds, then coming back after the scope is enabled/disabled.

**Comment by StriderTR** [comment]
Would it have anything to do with how the Pi is grounded? If I am not mistaken, the Pi grounds via HDMI to your monitor/TV. Not the same as your PC. Though I tried grounding mine to my PC and PSU chassis and got the same result. I'm just spitballing ideas, it's been a long day. lol

**Comment by EspoTek** [comment]
Genuinely no idea.  "Hard to reproduce" and "not critical" means I'll probably never know, sorry!

**Comment by theblaz** [comment]
I downloaded the Linux Legacy Appimage and I was able to calibrate no problem. Thanks for the suggestion and help.

**Comment by StriderTR** [comment]
Sadly, I don't see a way to get a legacy app image for Pi. Is it available anywhere?

Also, I did ground my Pi to my PC case with one of the GPIO grounds, it did affect the reading, but calibration still failed. Oh well, it was an idea. 

![lab-noground](https://user-images.githubusercontent.com/97561185/150282107-c3f1fe52-403c-4f8f-8c19-e6edfe28c8cf.jpg)
![lab-ground](https://user-images.githubusercontent.com/97561185/150282142-2899a162-9d3b-4a05-9259-b47249507675.jpg)

**Comment by EspoTek** [comment]
Finally had a bit of a lightbulb moment!
I think I know if not why, but at least when the issue was caused, and that it's part of the software.  I'll get a patch ready over the coming few days to roll back some of the changes that may have caused this regression!

**Comment by StriderTR** [comment]
Excellent! I'll give it a try once it's available. :)

**Comment by EspoTek** [comment]
It should be fixed now (keyword: should)!

Long story short, the patch that added the frequency spectrum was doing a whole lot of unnecessary maths when it wasn't enabled and overloading the Pi's tiny CPU, causing it to miss timing contraints.

I've pulled this out of the regular path (it now only runs when the spectrum mode is enabled) and it seems to be back to normal, at least from my end.

If other people are able to confirm this, I can fully close this off once and for all!

**Comment by StriderTR** [comment]
Calibration Successful!

Thanks for the fix! The Pi's tiny processor, and I, thank you! :P 

Perfect timing, the rest of the parts I ordered are arriving today so I will be able to give the Labrador a proper home. BNC connectors and probes for the scope, Banana connectors and probes for the multimeter and logic, and a clamp speaker type terminal block for the signal generator. All going in a simple black project enclosure. Once I have it all done I can take a nice pic and drop a proper review on Amazon.

Again, thanks for all your help! It's been greatly appreciated.

![2022-01-23-120333_1920x1080_scrot](https://user-images.githubusercontent.com/97561185/150692053-e1c4f92d-9b9d-47e9-a8bc-6779020ab317.jpg)

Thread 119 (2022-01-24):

### ISSUE TITLE
Working on Win 10 - but not on Android 8.0

### ISSUE THREAD

**Issue by Fixador** [EspoTek/Labrador#119]
Hi, fine on Win 10  , but using via an known good OTG into (1) Android 8.0 on a ZL10, and (2) Titan 4 . Android 5.01. The OTG lead was tested on both androids into a mouse. Labrador reports on both of the Androids  at the top of the screen that device not connected - red led is illuminated on pcb. Suggestions please

**Comment by superfrink** [comment]
Not sure if it is the same issue but I had to try four different micro USB cables until finding one that worked.

The setup was Android 9 with USB C -> OTG adapter to USB A -> USB cable to micro B -> Labrador.

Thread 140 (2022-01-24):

### ISSUE TITLE
Thought about making a more robust device/version 2?

### ISSUE THREAD

**Issue by cweagans** [EspoTek/Labrador#140]
The Labrador is great. It's really a huge accomplishment to have gotten it out the door, especially with how much functionality is packed into such a tiny space!

Have you thought about making version 2? And/or have you thought about making v2 a bigger/more full featured all-in-one device? I've been noodling on this and I think there's a pretty good market in the $100-200 range for a combination power supply/signal generator/oscope/logic analyzer. Here's my wishlist in the event that you're thinking about going down this road:

* Include a case with real ports for the various functions -- current device is good for breadboards and the like, but it would be cool to turn this into a bench tool. Display isn't needed, but having real ports for probes, PSU output, etc. would be cool!
* Bigger -- the current device is very portable, but is also easily lost in e.g. a pile of papers or whatever. Having a bigger, more substantial device would be awesome.
* More channels/higher data rate/etc -- generally just "more" across the board as it relates to the oscope/logic analyzer. I realize this wasn't ever meant to be a top-of-the-line device, but I'm curious about how far in that direction something like this could go with a bit more headroom in the budget? What's a sane number of channels/sample rate/etc?
* Same software -- the desktop client is really, really wonderful and I'd love to keep using it
* Fully variable PSU output - 0-60V up to 100W (which would allow for powering any PoE device, I think). Bonus points for making it possible to do more than one output for powering more complicated devices?
* USB-C -- I threw out all of my micro USB cables several years ago and now only have one for the Labrador. It would be awesome to standardize on USB-C across the board (and might help to accommodate higher sample rates and such too?)

That's most of my list, I think. If you're thinking about doing something like this, I'd love to collab on the software bits. Hardware isn't my forte just yet, but I'm learning.

**Comment by EspoTek** [comment]
The short answer is "yes, eventually".

Although I'd take the current software out the back and put a bolt through its skull before updating it for future hardware.  There are a lot of really short-sighted design choices that worked, but make it difficult to maintain long term.

**Comment by cweagans** [comment]
Fair enough! If you want help with the software bits, definitely hit me up. I’ve been very, very happy with Flutter and Dart if you’re looking for an alternative to the current setup.

**Comment by EspoTek** [comment]
The plan was actually to use Dear ImGui.
I'm not sure if you've used it before, but with a little bit of wrapper code to handle windowing and stuff cross-platform, it makes almost every class of GUI-related problem disappear.

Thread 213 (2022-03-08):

### ISSUE TITLE
'Batch 1' board "bricked" - scope not running

### ISSUE THREAD

**Issue by DeeJay** [EspoTek/Labrador#213]
I have a Batch 1 board purchased March 2018. I seem to have 'broken' it.

Yesterday I had it working with the current (Jan 2022) Windows continuous release of the Labrador software. (Should  have been content with that... )

Then I tried a build of Labrador for RasPiOS Bullseye 64-bit running on an RPi4B2G board. The Desktop interface appeared but reported "Device not detected". I did not investigate this in detail. 

Since then I have been unable to use the Labrador board with the previously-working MS Windows 10 installation. I have (apparently) successfully forced a Firmware Recovery by grounding the required pin and using the Help menu Recovery  option. But the 'scope function doesn't seem to run ('random' noise appears briefly then freezes) and attempts to calibrate always fail with a report of readings out of range. 

I have also tried reverting the Windows software to the legacy Update 1  and Update 2 releases,  but with no improvement. 

I think I have read all the relevant Documentation and tried all the Troubleshooting and Recovery tips. It feels as though  I have got the on-board processor into a state where it is no longer running correctly but cannot be reset?

Is there anything else I can do to breathe life into the little guy, or is this going to be a 29$ fix?

**Comment by EspoTek** [comment]
Hi mate, sounds like a bog standard bad flash.  Completely recoverable.

If you can get the board into bootloader mode, check out the two batch files under C:/Program Files/Espotek/EspoTek Labrador/Firmware

Run wipe.bat, then flash.bat and it should spring back to life.
If not, remove the wires that force it into bootloader mode then reconnect it twice.

If that doesn't fix it, shoot us an email and we can work it out together.

**Comment by DeeJay** [comment]
Just a brief comment to acknowledge that I mis-diagnosed my own problem.

I can confirm that the board itself is fine: the inability to run the 'scope - or any other data acquisition - seems to be a quirk in running the Windows interface on my Windows10 laptop.

I am in touch with  Chris via email to try to get a better understanding of why my HW/OS platform isn't being cooperative.

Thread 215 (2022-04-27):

### ISSUE TITLE
new board, after calibrate channel 1 always read around 1.667 volts and multimeter reads new 9v Alkaline at 10.1v

### ISSUE THREAD

**Issue by Mclute0** [EspoTek/Labrador#215]
am I missing something or am I getting stray voltage from somewhere?

my cheap multimeter reads the 9v battery at 8.7v, pretty sure 10.1v is just wrong.

AC coupling brings channel to zero.

the voltages below are all means.

touching the channel one probe to the USB ground show -0.12v

touch channel on to channel 2 no changes both on they both read 1.667v.

channel one to board + rail show 4.748v

channel one to - rail shows -0.03v

channel one multimeter to board - rail shows -1.6v with channel two to + rail also read 0.04 
channel one multimeter to board + rail shows 3.16v with channel two to - rail also reads 4.84

both channels read a ~60hz background oscillation at around .01 volts.

**Comment by EspoTek** [comment]
Hi mate, can you please attach a screenshot showing the 10.1V battery?

**Comment by Mclute0** [comment]
when first connecting the 9V battery, it always reads 3V for all three with no swings, but when I use the mouse wheel to scroll in or out it starts reading the 10V on a new battery and 7.9V on an older used battery with a +-0.02 volt swing.

![image](https://user-images.githubusercontent.com/101496003/159510660-7d895918-8808-4dcf-8013-12f8e6e21fe7.png)

**Comment by EspoTek** [comment]
Ahh, I see.  Make sure the trace is visible on the display; otherwise you may get issues with the amplifiers clipping.

**Comment by EspoTek** [comment]
And just to confirm, this is with CH1 (DC) on the positive terminal, and CH2 (DC) on the negative?

**Comment by Mclute0** [comment]
yes,  CH1 (DC) on the positive terminal, and CH2 (DC) on the negative. I also have not been able to get the interface to show uF. I,V,R show up, but changing to C and I get no F listed in the output stays at whatever the last reading was liike mV mA or resistance.

maybe I will take a look at the code and see if I see any issues, I used to do a little debugging for a living.

**Comment by Mclute0** [comment]
I is now giving F? without the μ? no numbers are sowing but minus sign comes are goes.

I see the display code and it looks pretty clean. I would guess this is a problem with the redraw data on window change procedures, that's without looking though all the code. still looking... The debug is showing cap_x1 == -1 that I take means no/bad reading from the board but it is transferring data of some kind.

![image](https://user-images.githubusercontent.com/101496003/159824202-ff02a688-91ab-4f5f-b20a-466a93b4ae98.png)

**Comment by EspoTek** [comment]
You'll need to set a resistance value to use R/C mode.
Please see the "Multimeter" section here:
https://github.com/EspoTek/Labrador/wiki

Cheers,
~Chris

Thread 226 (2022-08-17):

### ISSUE TITLE
Device will only measure 3 volts

### ISSUE THREAD

**Issue by JvilleJTW** [EspoTek/Labrador#226]
Trying to test my Labrador. Comparing it against my DMM on a simple circuit with an LED and resistor driven by a lab supply of 9 volts DC. DMM correctly shows 7.6 volts across resistor. Labrador in Multimeter mode shows 3V consistently. Using CH1, CH2 and Gnd. terminals hooked up to test leads. I have tried increasing voltage headroom, but this appears to only affect the onboard voltage supply. Neither DC scope channel makes any sense either. Using a Mac laptop.

**Comment by EspoTek** [comment]
Hi mate.  This isn't so much as a bug as questionable UI design.  Zoom out the scope trace so that the analog waveform is visible at 7.6V, and the digital display should start updating with the correct values too.

**Comment by JvilleJTW** [comment]
Chris--

This makes no sense. Neither the multimeter nor the scope are reading the correct figures. It's not close; they are off by 4-5 volts. I am abandoning this project.

JTW

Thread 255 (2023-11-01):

### ISSUE TITLE
Waveform generation clock settings

### ISSUE THREAD

**Issue by dbsamithey** [EspoTek/Labrador#255]
I think that line 219 of genericUsbDriver.cpp should be changed from 
`return CLOCK_FREQ / (division * channelData.samples.size() * channelData.freq);` 
to
`return CLOCK_FREQ / (division * channelData.samples.size() * channelData.freq) - 0.5;`

As I understand it, `CPS = CLOCK_FREQ / (division * channelData.samples.size() * channelData.freq)` is the appropriate number of clock cycles per waveform sample.  Also, it looks like the `PER` setting of the waveform generating timer is set to the value returned on line 219, which is `(int) CPS` in the current code.  But, the formula at the top of page 173 of the xmega-au manual indicates that the timer triggers every `(PER + 1)` clock cycles.  This means that `PER` should be set to `CPS-1` if `CPS` is an integer.  If `CPS` is not an integer, adding 0.5 to the result before returning it produces a `PER = (int) (CPS - 0.5)` that is rounded instead of truncated to the nearest integer.

The attached plots show the power spectra of nominally 5 khz sin waveforms generated by the Labrador both before (`PER = 75`) and after (`PER = 74`) the change to line 219 is made.  Before the change, the power spectrum peaks at 4,935 Hz, which corresponds to 76 clock cycles per waveform sample.  After the change, it properly peaks at 5,000 Hz, which corresponds to 75 clock cycles per waveform sample.
Before change:
![before_fix](https://github.com/EspoTek/Labrador/assets/127083957/66a8e5dc-b34f-45be-89b2-4c6ee4119a64)
After change:
![after_fix](https://github.com/EspoTek/Labrador/assets/127083957/c73315d2-e2e1-4b15-8884-c91c3eec5595)

**Comment by EspoTek** [comment]
Thanks so much for the write up.  I've had a few messages about slightly off frequencies, but have always come to the conclusion that it was just quantisation error (which, I suppose some of it is, but still).

I've committed the fix and it should upstream soon.

**Comment by dbsamithey** [comment]
No problem at all.  I'm glad I could make some small contribution to the device.  I think this also explains why the spectrum mode waveform breaks (#241) showed up for a nominally 1 khz signal.  Because the signal was actually 48e6 / (128 * 376) = 997.34 Hz, a phase difference ( [ 3 * 33 * (0.001 s) * (997.34 Hz)] mod 1 = 0.74 periods ) built up over the 3 missing frames.

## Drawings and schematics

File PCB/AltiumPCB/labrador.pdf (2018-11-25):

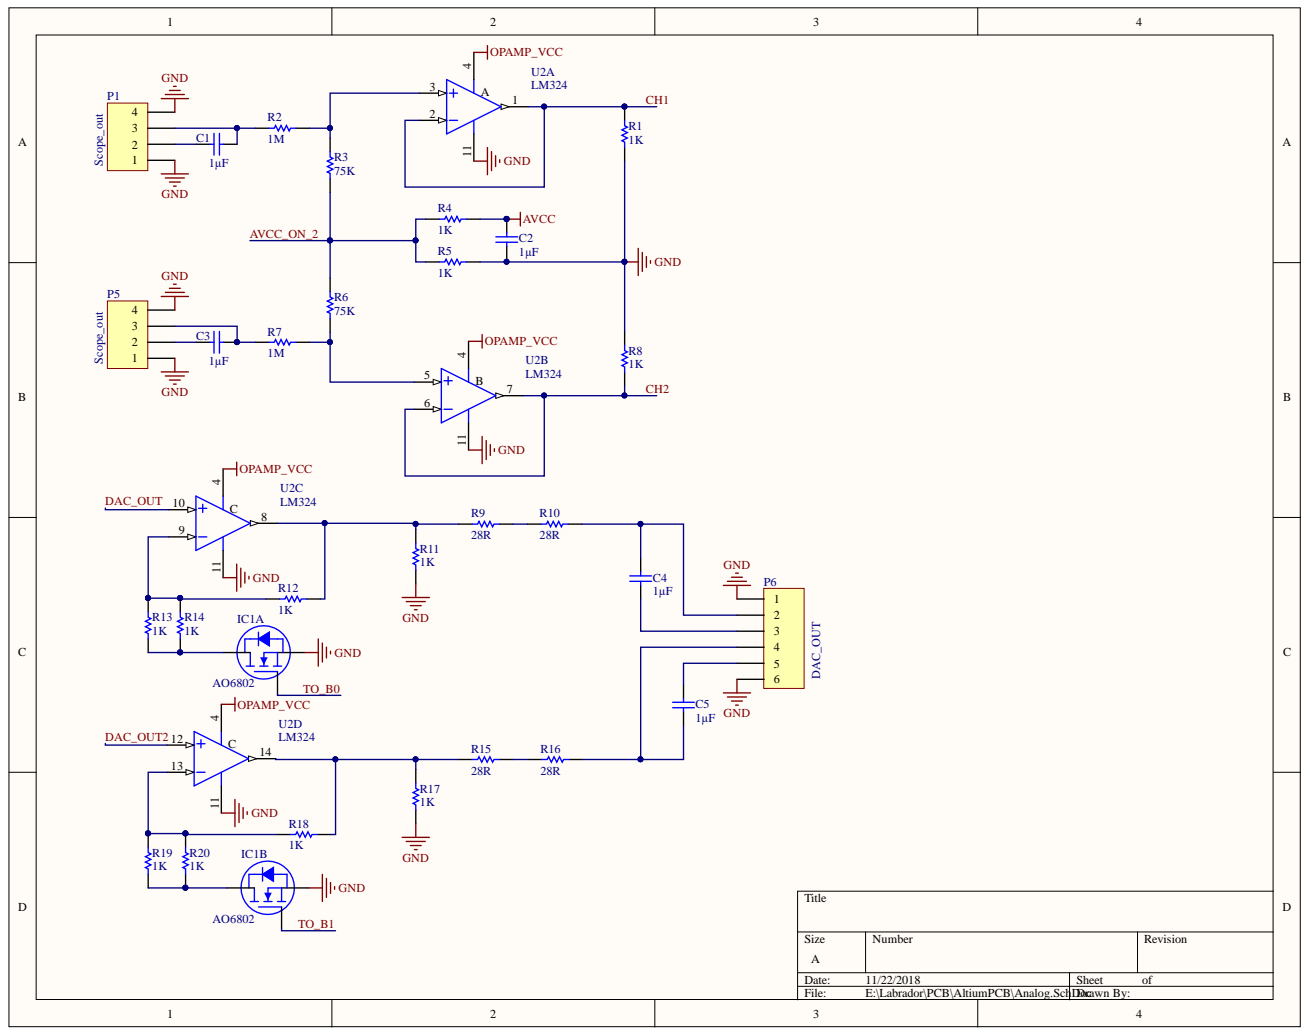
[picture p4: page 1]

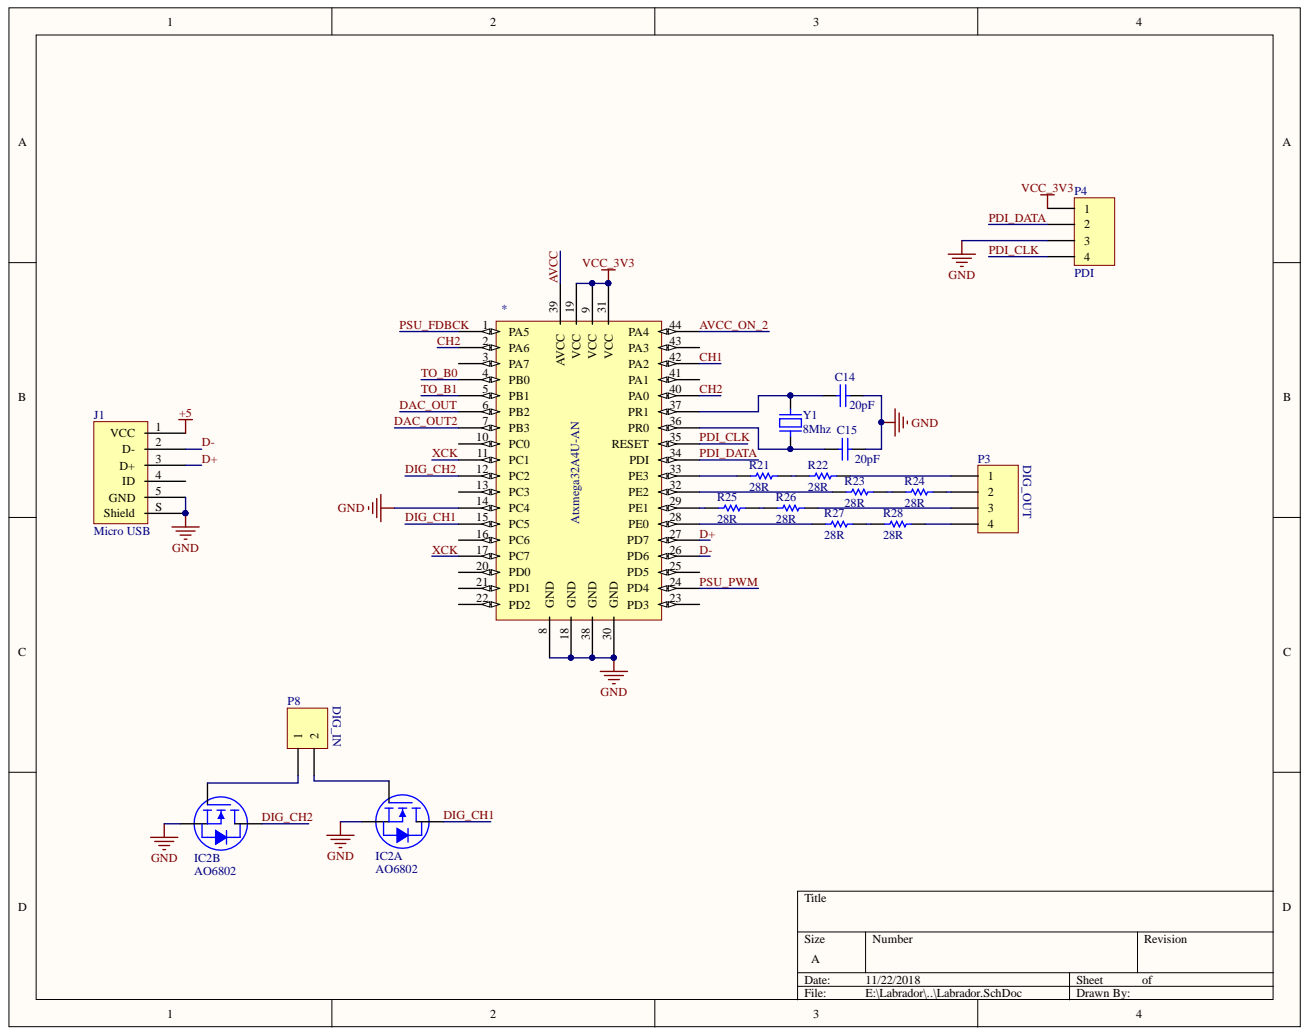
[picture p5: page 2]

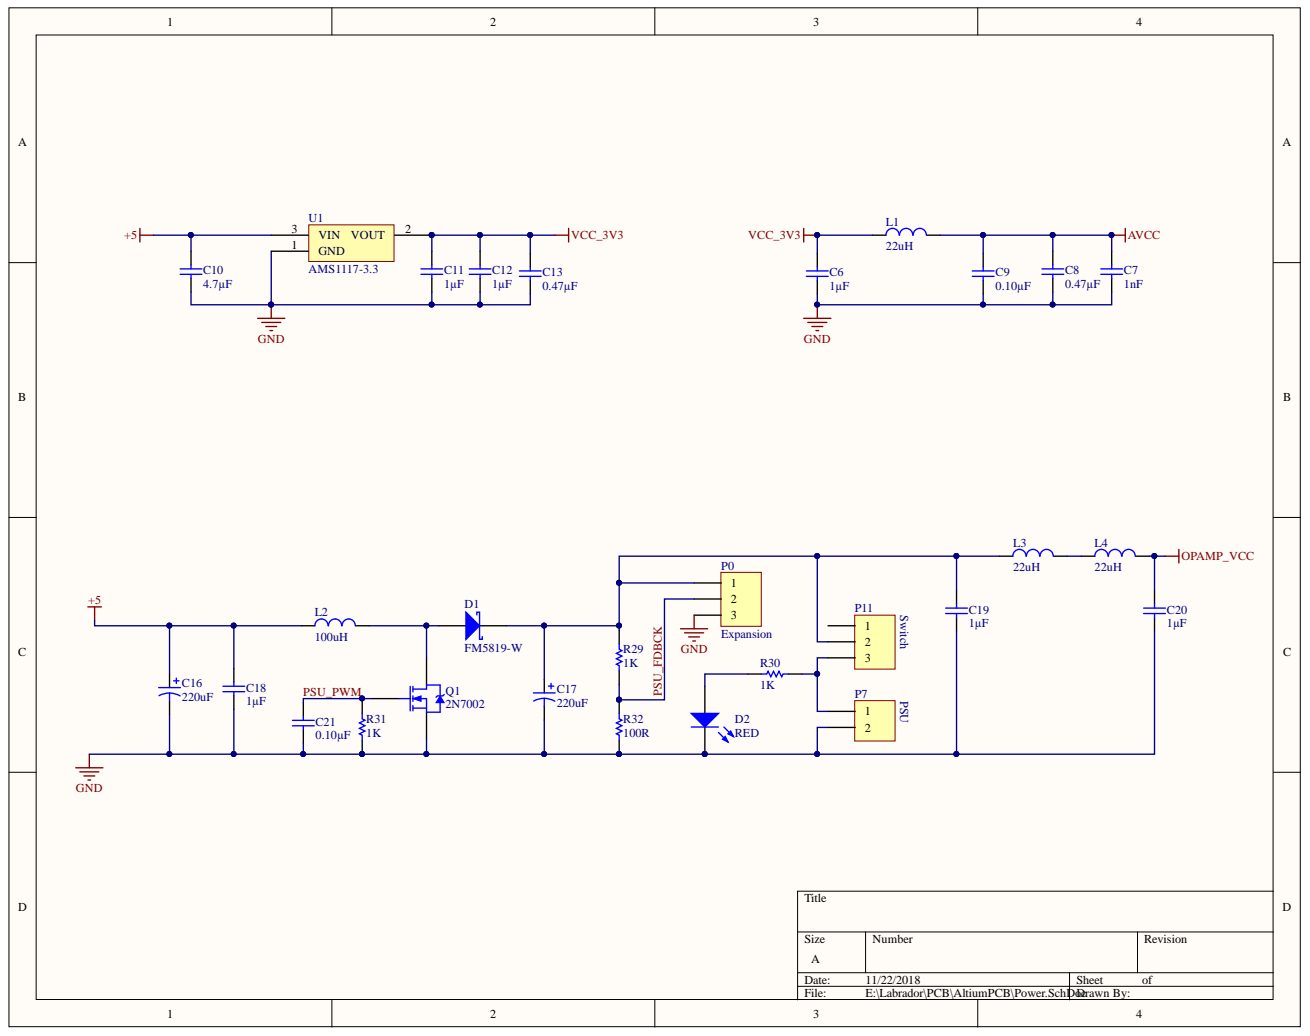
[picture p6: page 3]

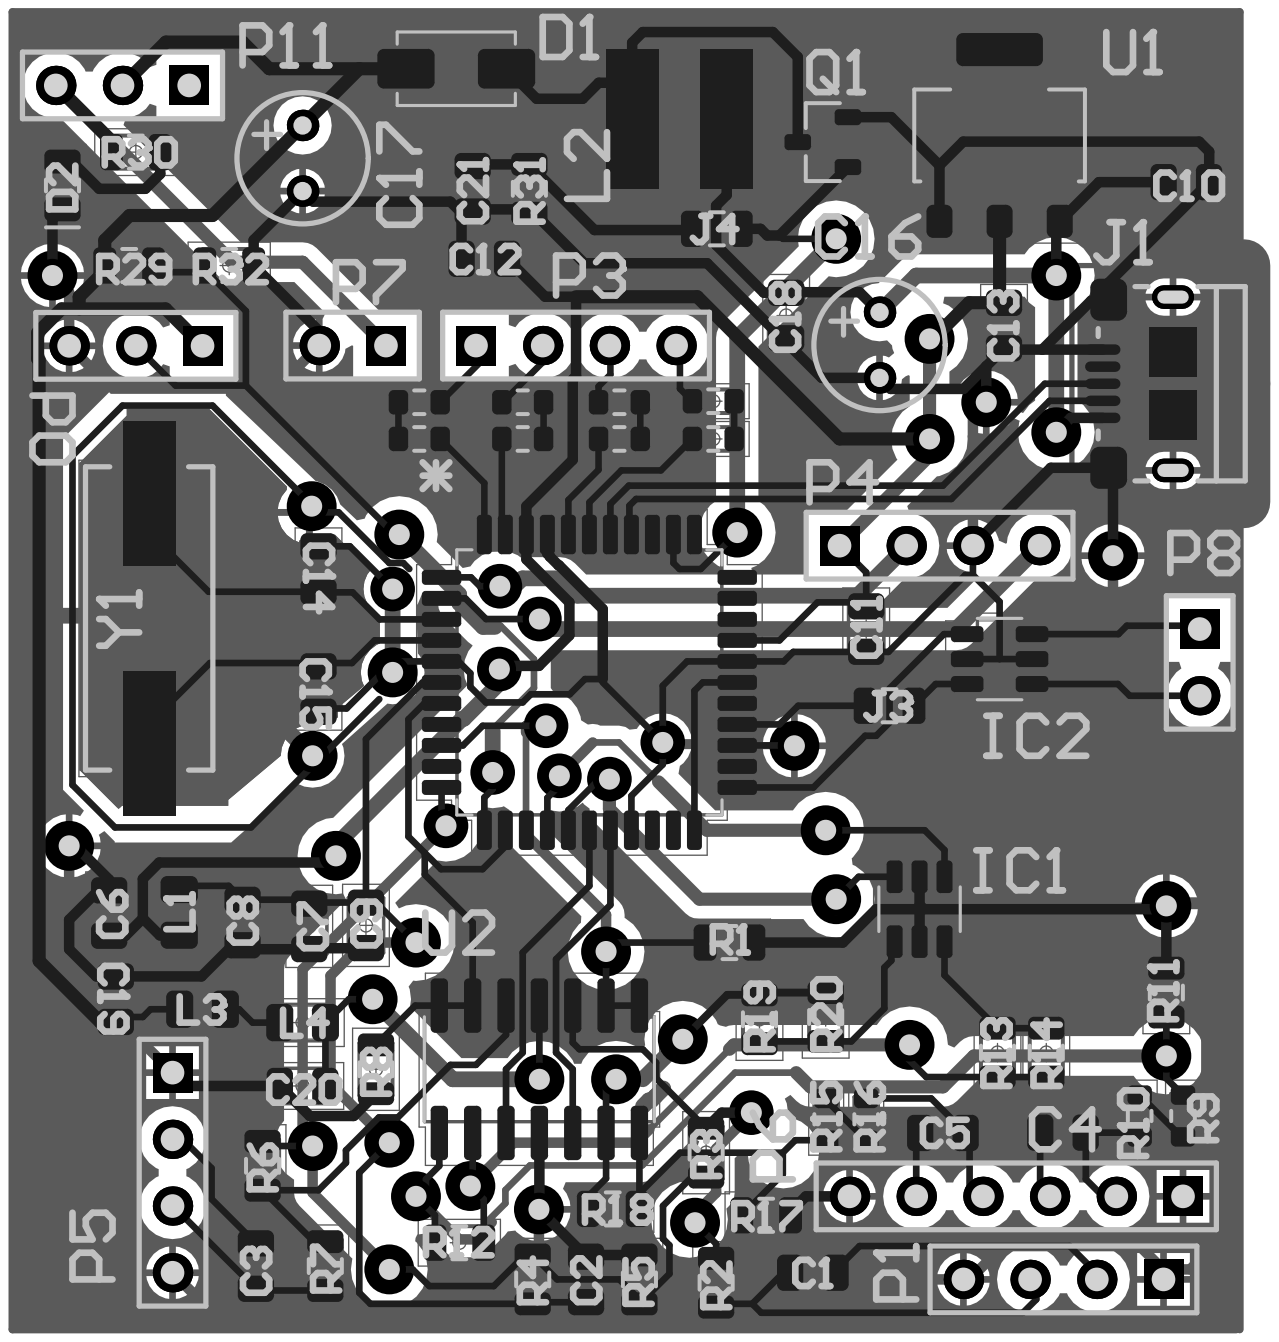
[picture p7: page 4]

# Board S

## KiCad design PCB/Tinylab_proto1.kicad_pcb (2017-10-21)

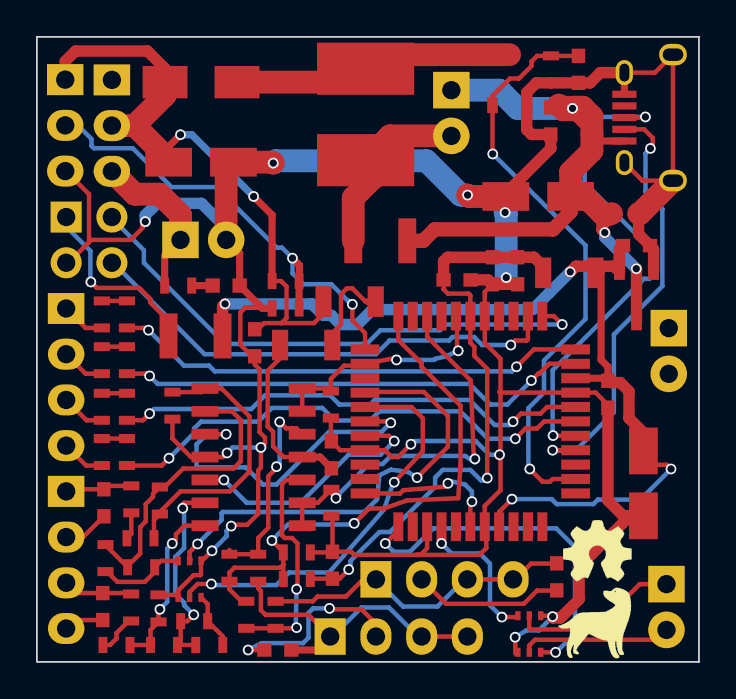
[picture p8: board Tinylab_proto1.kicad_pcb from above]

Board: 2 copper layers, 36.8 x 34.7 mm, 76 parts (0 on the bottom side), 60 nets.

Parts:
C1, C2, C7, C8, C10, C11, C12, C13, C14, C16, C17, C18: C; C_0603
C3, C4, C5: C_Small; C_0603
C6, C9, C15: CP1; c_elec_4x5.3
D1: D_Schottky; SMA_Standard
D2: LED; LED_0603
F1, F2: F_Small; C_1210
IC1: ATXMEGA32A4U-AU; LQFP-44_10x10mm_Pitch0.8mm
L1: INDUCTOR; SMALL_INDUCTOR
L2, L3, L4: INDUCTOR; R_1206
Main_Logo: LARGE_LOGO; logo175dpi
P1, P5: SCOPE_OUT; Pin_Header_Straight_1x04
P2: USB_OTG; USB_Micro-B_WIDE
P3: DIG_OUT; Pin_Header_Straight_1x04
P4: PDI/3V3; Pin_Header_Straight_2x02
P6: DAC_OUT; Pin_Header_Straight_1x04
P7: PSU; Pin_Header_Straight_1x02
P8: DIG_IN; Pin_Header_Straight_1x02
P9: FUSE_BYPASS; Pin_Header_Straight_1x02
P10: EXPANSION; Pin_Header_Straight_1x03
P11: SWITCH; Pin_Header_Straight_1x03
Q1: Q_NMOS_GSD; SOT-23-3
R1, R2: 1M; R_0603
R3, R4: 75K; R_0603
R5, R6, R15, R16, R17, R18, R19, R20, R21, R26, R28, R29, R30, R31, R32: 1K; R_0603
R7, R8, R9, R10, R11, R12, R13, R14, R22, R23, R24, R25: 28R; R_0603
R27: 100R; R_0603
U1: 78L05; SOT-23-3
U2: LM324; SOIC-14_3.9x8.7mm_Pitch1.27mm
U3, U4: DMN63D8LDW; SOT-363

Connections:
+5V: C3.1, C9.1, C10.1, F2.1, P2.1, P9.1, U1.3
/3V3_OUT: F1.1, P4.1
/AVCC: C5.1, C8.1, C17.1, C18.1, IC1.39, L2.2, R5.1
/AVCC_ON_2: IC1.44, R3.2, R4.1, R5.2, R6.2
/Buffered_DAC_CH1: R19.1, R22.2, R29.1, U2.8
/Buffered_DAC_CH2: R20.1, R23.2, R30.2, U2.14
/CH1: IC1.42, R21.1, U2.1, U2.2
/CH2: IC1.2, IC1.40, R28.2, U2.6, U2.7
/D0-prefuse: IC1.28, R11.1
/D0_MID: R7.1, R11.2
/D0_OUT: P3.4, R7.2
/D1-prefuse: IC1.29, R12.1
/D1_MID: R8.1, R12.2
/D1_OUT: P3.3, R8.2
/D2-OUT: P3.2, R9.2
/D2-prefuse: IC1.32, R13.1
/D2_MID: R9.1, R13.2
/D3-OUT: P3.1, R10.2
/D3-prefuse: IC1.33, R14.1
/D3_MID: R10.1, R14.2
/D+: IC1.27, P2.3
/D-: IC1.26, P2.2
/DAC_OUT: IC1.6, U2.10
/DAC_OUT2: IC1.7, U2.12
/DIG_CH1: IC1.15, U4.6
/DIG_CH2: IC1.12, U4.3
/L-Ana_IN_CH1: P8.1, U4.5
/L-Ana_IN_CH2: P8.2, U4.2
/OPAMP_VCC: C16.1, L4.1, U2.4
/PDI_CLK: IC1.34, P4.2
/PDI_DATA: IC1.35, P4.4
/PSU_FDBK: IC1.1, P10.2, R26.2, R27.1
/PSU_OUT: P7.1, P11.3, R32.1
/PSU_PWM: C12.1, IC1.24, Q1.1, R31.1
/PSU_Unfiltered_Raw: C7.1, C15.1, D1.1, L3.2, P10.1, P11.2, R26.1
/QTop: D1.2, L1.1, Q1.3
/R22-R24: R22.1, R24.2
/R23-R25: R23.1, R25.2
/S-Gen_CH1_AC: C13.1, P6.2
/S-Gen_CH1_DC: C13.2, P6.1, R24.1
/S-Gen_CH2_AC: C14.1, P6.4
/S-Gen_CH2_DC: C14.2, P6.3, R25.1
/S-Gen_Drain_Top_CH1: R17.2, R18.2, U3.3
/S-Gen_Drain_Top_CH2: R15.2, R16.2, U3.6
/Scoe_CH1_AC: C1.2, P1.2
/Scope_Buffer_Input_CH1: R1.1, R3.1, U2.3
/Scope_Buffer_Input_CH2: R2.1, R4.2, U2.5
/Scope_CH1_DC: C1.1, P1.1, P1.3, P1.4, R1.2
/Scope_CH2_AC: C2.2, P5.2
/Scope_CH2_DC: C2.1, P5.1, P5.3, P5.4, R2.2
/TO_B0: IC1.4, U3.2
/TO_B1: IC1.5, U3.5
/VCC_3V3: C4.1, C6.1, C11.1, F1.2, IC1.19, IC1.31, L2.1, U1.2
/VGND: C3.2, C4.2, C5.2, C6.2, C7.2, C8.2, C9.2, C10.2, C11.2, C12.2, C15.2, C16.2, C17.2, C18.2, D2.1, IC1.8, IC1.14, IC1.18, IC1.30, IC1.38, P2.5, P2.6, P4.3, P7.2, P10.3, Q1.2, R6.1, R21.2, R27.2, R28.1, R29.2, R30.1, R31.2, U1.1, U2.11, U3.1, U3.4, U4.1, U4.4
/V_minus_dac_out: R17.1, R18.1, R19.2, U2.9
/V_minus_dac_out2: R15.1, R16.1, R20.2, U2.13
/XCK: IC1.11, IC1.17
unnamed: D2.2, R32.2
unnamed: F2.2, L1.2, P9.2
unnamed: L3.1, L4.2

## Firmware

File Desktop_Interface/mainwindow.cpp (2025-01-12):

#include "mainwindow.h"
#include "uartstyledecoder.h"
#include "daqform.h"
#include <QDesktopServices>
#include "espospinbox.h"

#include <algorithm>

#define DO_QUOTE(X) #X
#define QUOTE(X) DO_QUOTE(X)

#ifndef GIT_HASH_SHORT
#define GIT_HASH_SHORT 0000000
#endif

namespace
{
   constexpr uint32_t MAX_CONSOLE_BLOCK_COUNT = 512;
   constexpr char kDocumentationUrl[] = "https://github.com/EspoTek/Labrador/wiki";
   constexpr char kPinoutUrl[] = "https://github.com/EspoTek/Labrador/wiki/Pinout";
   constexpr char kAboutString[] = "<h4>EspoTek Labrador</h4>"
                                   "Continuous Release<br>"\
                                   "Git hash: <a href='https://github.com/EspoTek/Labrador/commits/" QUOTE(GIT_HASH_SHORT) "'>" QUOTE(GIT_HASH_SHORT) "</a><br>"\
                                   "Website: <a href='http://espotek.com'>https://espotek.com</a><br>"\
                                   "Contact email: <a href='mailto:admin@espotek.com'>admin@espotek.com</a>";
   constexpr char kOrganisationName[] = "EspoTek";
   constexpr char kApplicationName[] = "Labrador";
}

MainWindow::MainWindow(QWidget *parent) :
    QMainWindow(parent),
    ui(new Ui::MainWindow)
{
    defaultPalette = qApp->palette();
    defaultStyleName = qApp->style()->objectName();

    QCoreApplication::setOrganizationName(kOrganisationName);
    QCoreApplication::setApplicationName(kApplicationName);

    ui->setupUi(this);

    calibrationMessages = new QMessageBox();
    ui->psuDisplay->display("4.00");
    ui->bufferDisplay->refreshImage();

    ui->waveformSelect_CH1->readWaveformList();
    ui->waveformSelect_CH2->readWaveformList();

    labelPsu();

    ui->psuDisplay->display("4.50");

    ui->controller_iso->setDriver(new _PLATFORM_DEPENDENT_USB_OBJECT());
    ui->controller_iso->setAxes(ui->scopeAxes);

    ui->timeBaseSlider->setMaximum(10*log10(MAX_WINDOW_SIZE));

    //ui->controller_iso->driver->setBufferPtr(ui->bufferDisplay);
    ui->cursorStatsLabel->hide();
    initialisePlot();
    menuSetup();
    readSettingsFile();

    ui->voltageInfoMaxDisplay_CH1->display(5312);
    ui->voltageInfoMinDisplay_CH1->display(0.01);
    ui->voltageInfoMeanDisplay_CH1->display(0.02);
    ui->voltageInfoRmsDisplay_CH1->display(6.00);
    connectDisplaySignals();

    ui->controller_iso->internalBuffer375_CH1->m_console1 = ui->console1;
    ui->controller_iso->internalBuffer375_CH1->m_console2 = ui->console2;

    ui->controller_iso->internalBuffer375_CH2->m_console1 = ui->console1;
    ui->controller_iso->internalBuffer375_CH2->m_console2 = ui->console2;
    initShortcuts();

    ui->debugButton1->setVisible(0);
    ui->debugButton2->setVisible(0);
    ui->debugButton3->setVisible(0);
    ui->debugConsole->setVisible(0);

//    // Set the consoles to be resizeable
//    for (const auto & console : {ui->console1, ui->console2})
//    {
//        console->setWindowFlags(Qt::SubWindow);
//        QSizeGrip* sizeGrip = new QSizeGrip(console);
//        QGridLayout* layout = new QGridLayout(console);
//        layout->addWidget(sizeGrip, 0,0,1,1,Qt::AlignBottom | Qt::AlignLeft);
//    }

    for (const auto & console : {ui->console1, ui->console2, ui->txuart})
    {
        QFont font("Monospace");
        font.setStyleHint(QFont::Monospace);
        console->setFont(font);
    }

#ifndef PLATFORM_ANDROID
    ui->kickstartIsoButton->setVisible(0);
    ui->console1->setVisible(0);
    ui->console2->setVisible(0);
    ui->txuart->setVisible(0);
#endif
    ui->timeBaseSlider->setVisible(0);

    //ui->pausedLabel_CH2->setVisible(0);
    ui->filterLabel_CH1->setVisible(0);
    ui->filterLabel_CH2->setVisible(0);

    //Reset the device to ensure Labrador_libusbk gets handle!!
    #ifdef PLATFORM_WINDOWS
        //ui->controller_iso->driver->usbSendControl(0x40, 0xa7, 0, 0, 0, NULL);
        //reinitUsb();
        ui->controller_iso->driver->killOnConnect = true;
    #endif
    #ifdef PLATFORM_LINUX
        reinitUsb();
    #endif
    #ifdef PLATFORM_MAC
        reinitUsb();
    #endif
    #ifdef PLATFORM_ANDROID
        ui->actionAutomatically_Enable_Cursors->setVisible(false);
        //hide second pause label
        ui->pausedLabel_CH2->setVisible(false);
        //Capture pinches
        ui->scopeAxes->grabGesture(Qt::PinchGesture);
        ui->scopeAxes->installEventFilter(this);
        //Mutually exclude pinches/cursors
        connect(ui->scaleHoriCheck, SIGNAL(clicked(bool)),
                   this, SLOT(horiScaleEvent(bool)));
        connect(ui->scaleVertCheck, SIGNAL(clicked(bool)),
                   this, SLOT(vertScaleEvent(bool)));
        //Screen Rotation.  Thanks, Hamlet.  https://forum.qt.io/topic/66240/how-to-detect-rotate-on-android
        screenPtr = QGuiApplication::primaryScreen();
            connect(screenPtr, SIGNAL(orientationChanged(Qt::ScreenOrientation)),
                       this, SLOT(screenRotateEvent(Qt::ScreenOrientation)));

             screenPtr->setOrientationUpdateMask(
                        Qt::PortraitOrientation
                        | Qt::LandscapeOrientation
                        | Qt::InvertedPortraitOrientation
                        | Qt::InvertedLandscapeOrientation);

        //Hide the PSU page
        ui->stackedWidget->removeWidget(ui->page_5);

        //Reconnect the other objects.
        //ui->controller_iso->driver->setBufferPtr(ui->bufferDisplay);
        connect(ui->debugButton1, SIGNAL(clicked()), ui->controller_iso->driver, SLOT(avrDebug()));
        connect(ui->psuSlider, SIGNAL(voltageChanged(double)), ui->controller_iso->driver, SLOT(setPsu(double)));
        connect(ui->controller_iso, SIGNAL(setGain(double)), ui->controller_iso->driver, SLOT(setGain(double)));
        connect(ui->controller_fg, &functionGenControl::functionGenToUpdate, ui->controller_iso->driver, &genericUsbDriver::setFunctionGen);
        connect(ui->bufferDisplay, SIGNAL(modeChange(int)), ui->controller_iso->driver, SLOT(setDeviceMode(int)));
		connect(ui->bufferDisplay, &bufferControl::modeChange, this, [this](){
			// Force a trigger refresh
			ui->controller_iso->setTriggerLevel(ui->triggerLevelValue->value());	
		});
        connect(ui->bufferDisplay, SIGNAL(updateDig(int)), ui->controller_iso->driver, SLOT(newDig(int)));

        //Set the settings again!
        connect(ui->controller_iso->driver, SIGNAL(gainBuffers(double)), ui->controller_iso, SLOT(gainBuffers(double)));
        connect(ui->controller_iso->driver, SIGNAL(disableWindow(bool)), this, SLOT(setEnabled(bool)));
        connect(ui->controller_iso->driver, SIGNAL(sendClearBuffer(bool,bool,bool)), ui->controller_iso, SLOT(clearBuffers(bool,bool,bool)));
        //connect(ui->controller_iso->driver, SIGNAL(startIsoTimer()), ui->controller_iso, SLOT(startTimer()));
        connect(ui->controller_iso->driver, SIGNAL(setVisible_CH2(bool)), ui->controller_iso, SLOT(setVisible_CH2(bool)));
        //connect(ui->controller_iso->driver, SIGNAL(enableMMTimer()), ui->controller_iso, SLOT(enableMM()));
        connect(ui->controller_iso->driver, SIGNAL(checkXY(bool)), ui->xyDisplayLabel, SLOT(setChecked(bool)));
        connect(ui->controller_iso->driver, SIGNAL(disableWindow(bool)), ui->deviceConnected, SLOT(connectedStatusChanged(bool)));
        connect(ui->controller_iso->driver, SIGNAL(upTick()), ui->controller_iso, SLOT(timerTick()));
        connect(ui->controller_iso->driver, SIGNAL(connectedStatus(bool)), ui->deviceConnected, SLOT(connectedStatusChanged(bool)));
        connect(ui->controller_iso->driver, SIGNAL(signalFirmwareFlash(void)), ui->deviceConnected, SLOT(flashingFirmware(void)));

        ui->serialDecodingModeSelect_CH1->setVisible(false);
        ui->serialDecodingModeSelect_CH2->setVisible(false);

        QTimer::singleShot(30, this, SLOT(dpiAutoScaling()));

        ui->androidMenuButton->setVisible(false);


        ui->menuAndroid_Special->menuAction()->setVisible(false);
    #endif

    connect(ui->controller_iso->driver, SIGNAL(killMe()), this, SLOT(reinitUsb()));
    ui->console1->setMaximumBlockCount(MAX_CONSOLE_BLOCK_COUNT);
    ui->console2->setMaximumBlockCount(MAX_CONSOLE_BLOCK_COUNT);
    //ui->frequencyValue_CH2->setValue(369);
    //ui->amplitudeValue_CH2->setValue(2);
    ui->controller_iso->doNotTouchGraph = false;

#ifndef PLATFORM_ANDROID
    ui->multimeterRLabel->setVisible(false);
    ui->multimeterRComboBox->setVisible(false);
#endif

    connect(ui->controller_iso, SIGNAL(multimeterREnabled(int)), this, SLOT(rSourceIndexChanged(int)));
    connect(ui->controller_iso, SIGNAL(multimeterRMS(double)), ui->multimeterRmsDisplay, SLOT(display(double)));
    connect(ui->controller_iso, SIGNAL(sendMultimeterLabel4(QString)), ui->multimeterRmsLabel, SLOT(setText(QString)));
    connect(ui->controller_iso, SIGNAL(sendVRMS_CH1(double)), ui->voltageInfoRmsDisplay_CH1, SLOT(display(double)));
    connect(ui->controller_iso, SIGNAL(sendVRMS_CH2(double)), ui->voltageInfoRmsDisplay_CH2, SLOT(display(double)));

    connect(ui->controller_iso, SIGNAL(mainWindowPleaseDisableSerial(int)), this, SLOT(serialEmergencyDisable(int)));

    connect(ui->controller_iso->driver, SIGNAL(signalFirmwareFlash(void)), ui->deviceConnected, SLOT(flashingFirmware(void)));
    connect(ui->controller_iso->internalBuffer375_CH1, SIGNAL(fileIOinternalDisable()), this, SLOT(fileLimitReached_CH1()));
    connect(ui->controller_iso->internalBuffer750, SIGNAL(fileIOinternalDisable()), this, SLOT(fileLimitReached_CH1()));
    connect(ui->controller_iso->internalBuffer375_CH2, SIGNAL(fileIOinternalDisable()), this, SLOT(fileLimitReached_CH2()));

    connect(ui->controller_iso, SIGNAL(showRealtimeButton(bool)), ui->realTimeButton, SLOT(setVisible(bool)));
    connect(ui->realTimeButton, SIGNAL(pressed()), ui->controller_iso, SLOT(disableFileMode()));


	
    connect(ui->pausedLabeL_CH1, SIGNAL(toggled(bool)), this, SLOT(paused(bool)));
    connect(ui->pausedLabel_CH2, SIGNAL(toggled(bool)), this, SLOT(paused(bool)));
    connect(ui->pause_LA, SIGNAL(toggled(bool)), this, SLOT(paused(bool)));
    connect(ui->multimeterPauseCheckBox, SIGNAL(toggled(bool)), this, SLOT(paused(bool)));

#ifndef PLATFORM_ANDROID
    connect(ui->hideCH1Box, SIGNAL(toggled(bool)), ui->controller_iso, SLOT(hideCH1(bool)));
    connect(ui->hideCH2Box, SIGNAL(toggled(bool)), ui->controller_iso, SLOT(hideCH2(bool)));

    connect(ui->actionHexDisplay, &QAction::toggled, ui->controller_iso, &isoDriver::setHexDisplay_CH1);
    connect(ui->actionHexDisplay_2, &QAction::toggled, ui->controller_iso, &isoDriver::setHexDisplay_CH2);

	ui->hideCH1Box->setVisible(false);
	ui->hideCH2Box->setVisible(false);
#endif
    ui->realTimeButton->setVisible(false);

    if ((QApplication::desktop()->availableGeometry().width() < 1520) || (QApplication::desktop()->geometry().height() < 800))
    {
        qDebug() << "Low resolution detected:" << QApplication::desktop()->availableGeometry().width() << "x" << QApplication::desktop()->availableGeometry().height();
        this->setMinimumSize(1280, 700);
        this->resize(1280, 700);
    }
    else
    {
        this->setMinimumSize(1520, 800);
        this->resize(1520, 800);
    }
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

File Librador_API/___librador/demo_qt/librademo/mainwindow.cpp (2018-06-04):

#include "mainwindow.h"
#include "ui_mainwindow.h"
#include "librador.h"
#include "QDebug"
#include <QVector>
#include "qcustomplot.h"

MainWindow::MainWindow(QWidget *parent) :
    QMainWindow(parent),
    ui(new Ui::MainWindow)
{
    ui->setupUi(this);
    setbuf(stdout, 0);
    setbuf(stderr, 0);
    initialisePlot();
}

MainWindow::~MainWindow()
{
    delete ui;
}

void MainWindow::initialisePlot()
{
    ui->widget->addGraph();
    ui->widget->addGraph();

    ui->widget->yAxis->setAutoTickCount(9);
    ui->widget->xAxis->setAutoTickCount(9);

    ui->widget->graph(0)->setPen(QPen(Qt::yellow, 1));
    ui->widget->graph(1)->setPen(QPen(Qt::cyan, 1));

    ui->widget->xAxis->setBasePen(QPen(Qt::white, 1));
    ui->widget->yAxis->setBasePen(QPen(Qt::white, 1));
    ui->widget->xAxis->setTickPen(QPen(Qt::white, 1));
    ui->widget->yAxis->setTickPen(QPen(Qt::white, 1));
    ui->widget->xAxis->setSubTickPen(QPen(Qt::white, 1));
    ui->widget->yAxis->setSubTickPen(QPen(Qt::white, 1));
    ui->widget->xAxis->setTickLength(6);
    ui->widget->yAxis->setTickLength(6);
    ui->widget->xAxis->setSubTickLength(4);
    ui->widget->yAxis->setSubTickLength(4);
    ui->widget->xAxis->setTickLabelColor(Qt::white);
    ui->widget->yAxis->setTickLabelColor(Qt::white);

    ui->widget->setBackground(Qt::black);


    ui->widget->replot();
}


void MainWindow::on_pushButton_clicked()
{
    qDebug() << librador_init();
}

void MainWindow::on_pushButton_2_clicked()
{
    qDebug() << librador_exit();
}

void MainWindow::on_pushButton_3_clicked()
{
    qDebug() << librador_setup_usb();
}

void MainWindow::on_pushButton_4_clicked()
{
    qDebug() << librador_avr_debug();
}

void MainWindow::on_pushButton_5_clicked()
{
    double sampleRate = 375000;
    if((current_channel == 1) || (current_channel == 2)){
        std::vector<double> *from_librador = (librador_get_analog_data(current_channel, 1, sampleRate, 0.1, 0));
        plot_from_librador(from_librador, sampleRate, ui->widget->graph(0));
    } else {
        std::vector<double> *from_librador_ch1 = (librador_get_analog_data(1, 1, sampleRate, 0.1, 0));
        std::vector<double> *from_librador_ch2 = (librador_get_analog_data(2, 1, sampleRate, 0.1, 0));
        plot_from_librador(from_librador_ch1, sampleRate, ui->widget->graph(0));
        plot_from_librador(from_librador_ch2, sampleRate, ui->widget->graph(1));
    }
}


void MainWindow::on_pushButton_6_clicked()
{
    qDebug() << librador_reset_usb();
}

void MainWindow::on_pushButton_7_clicked()
{
    qDebug() << librador_get_device_firmware_version();
}

void MainWindow::on_pushButton_8_clicked()
{
    qDebug() << librador_get_device_firmware_variant();
}

void MainWindow::on_pushButton_9_clicked()
{
    qDebug() << librador_set_power_supply_voltage(ui->powerSupplySpinBox->value());
}

void MainWindow::on_checkBox_stateChanged(int arg1)
{
    qDebug() << librador_set_digital_out(1, arg1);
}

void MainWindow::on_checkBox_2_stateChanged(int arg1)
{
    qDebug() << librador_set_digital_out(2, arg1);
}

void MainWindow::on_checkBox_3_stateChanged(int arg1)
{
    qDebug() << librador_set_digital_out(3, arg1);
}

void MainWindow::on_checkBox_4_stateChanged(int arg1)
{
    qDebug() << librador_set_digital_out(4, arg1);
}

void MainWindow::on_comboBox_activated(int index)
{
    double gainValues[8] = {0.5, 1, 2 , 4, 8, 16, 32, 64};
    qDebug() << index;

    double newGain = gainValues[index];
    ymax = 1.65 + (11/newGain);
    ymin = 1.65 - (14/newGain);
    qDebug() << librador_set_oscilloscope_gain(newGain);
}

void MainWindow::on_pushButton_10_clicked()
{
    qDebug() << librador_reset_device();
}

void MainWindow::on_pushButton_11_clicked()
{
    qDebug() << librador_jump_to_bootloader();
}
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

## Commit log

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2016-09-26 Board update and start of CSV export
    Some CSV export features implemented - dump everything (in a stream -
    750ksps!!) or just dump what's visible in screen. Stream doesn't dump
    actual voltage readings but raw sample data.
    Board software has been updated to fix DMAnot transmitting the correct
    data for signal gen CH1 in modes 4 and 5
    Former-commit-id: 7f40f04ef9ef661a6abecaf98945b168c981361a
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2016-10-04 Proper fix for bug
    Never sets device mode to 5 now, preventing frequency from changing when
    scope disabled.
    Former-commit-id: ae34eaf6929f6c18a37ac20ce7837450ed57654f
2016-10-13 Bugfix
    Quick bugfix in AVR code. Prevents CH1 accidentally controlling sample
    number on CH2.
    Former-commit-id: ce0d5b8bb16e0fe0f1c60779f0f0f5842e644d4e
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2016-10-24 Linux version up and running, with autorecover!
    Hopefully the Windows compile hasn't been broken. Fingers crossed!
    Former-commit-id: 8b9928936988402fcdf9141cb555189d9b0a552e
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2016-11-09 Mac OS X build running
    May have accidentally broken Linux (untested, I wasn’t being shotgunny
    but equally wasn’t being super careful). Seems to randomly fail on
    launch. Probably a race condition on the mutex?
    Former-commit-id: b7e0035896728a3bd2c35f094e633e353fe8a610
2016-11-10 Added a single #define
    That's it. Literally a single #define that determines how many
    milliseconds the OS waits before reconnecting. Fixed an error with
    Windows not reading it on new mobo, hopefully fixes it under OS X as
    well.
    Former-commit-id: d69bbf8e683c48ba4cbfb10b0e14d975f80f0c37
2016-11-19 Reverted PCB files to initial upload
    Going to have a final attempt now!
    Former-commit-id: bf98f0796f133ae306d1ae27333cd226d25ba464
2016-11-19 Undid PCB revert
    I don't want to deal with KiCAD's library management again. The first
    time was bad enough.
    Former-commit-id: 2696688130524c5450ddf9dd3b6a964ddf03b398
2016-11-20 New Eschema
    - Reverted the dual transistor IC back to a single transistor (TSM
    thingo)
    - Added PSU indicator LED
    - Added PSU control/expansion header.
    Note that this is only in eschema, not pcbnew!
    Former-commit-id: 059d5cbe658ad929d363e2eeb488671389c9f054
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2016-11-21 Swapped all components to SMD
    Board too dense. Going to start again.
    Former-commit-id: edf9c8904b3d58a564246fe7ac94ae7e57a7f3ba
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2016-11-22 FInished the board.
    Just need to position balange pins. Design seems tight, with really low
    power supply distances.
    Former-commit-id: 0964cc7e6adbb0a126274a3b8bd1637333d6df1d
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2016-11-27 Added more #defines to code
    These #defines are located in desktop_settings.h and allow you to edit
    how many samples are discarded per packet. The idea was to use this to
    test the MCU-side code and ensure that it doesn't corrupt a packet per
    frame, but this seems to have magically disappeared (???).
    I remember queueing USB transfers a long time ago, but can't remember
    this having any success. It's more likely to just be a random clock
    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
2016-12-07 Sped up serial decode dramatically
    Swapped an append to a replace with an ADT designed to return fast
    pointers to char[] blocks.
    Worked out that the one-corrupt-sample-per-packet bug was definitely not
    fixed. I must have been looking at a 1kHz wave before.
    Former-commit-id: d3054d9707670e2b333b377888c7534a92e91d4f
2016-12-07 3 lines changed
    Just to make debugging easier on the one-packet-per-frame-dropped error.
    Former-commit-id: 88ddd41c8dc7c97e1ef9335a3a8aa462b9d23ccf
2016-12-12 3 Iso Endpoints
    Have moved from one big (1023 byte) iso endpoint to 3x 256 byte ones.
    This will fix the error where Labrador is picky about which port it's
    connected to, and *should* fix the one-sample-per-packet error.
    Former-commit-id: 880303ed09c8363c591095ab78444999fb9502e5
2016-12-14 Triple endpoints working in SW now
    Added triple endpoint support for the Desktop interface.
    Should be possible to fix the one-packet-per-sample glitch easily, now.
    Even if it isn't, the device now only needs to reserve 768 bytes/frame,
    not 1023!!!!
    Former-commit-id: 5769288a1141ba42771ba3fd4fe8e8a88aafa714
2016-12-15 One packet per sample glitch gone!!!
    From the looks of things, anyway.
    This fix came with a cost:
    - All modes apart from 0 are broken.
    - Randomly, the DMA write and USB read may access the same half of
    isoBuf. This is determined on boot, and doesn't seem to desynchronise
    and resynchronise over time.
    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
2016-12-18 And mode 7 up
    Bugs found recently:
    - Trigger doesn't work on negative voltages (at least in MM mode).
    - Double Sample Rate button won't de-trigger when CH1 scope is disabled.
    Former-commit-id: 56f329a016420c3f6c2e368fd2c8f08b11a0d4c0
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2017-02-05 Removed delays from winUsbDriver's Iso stack - other half of software bug fixed?
    No longer seems to show that "every packet is corrupt" error. I suspect
    it was caused by the "filling the transfer contents" loop in
    usbIsoInit() taking place during two 1ms periods. This would, in
    theory, cause it to skip over 1ms of data every ISO_PACKETS_PER_CTX *
    NUM_FUTURE_CTX frames.
    Former-commit-id: 66a8b96e10853073b93f976bf17f3b93e74480b9
2017-02-06 Quick PCB finalisationsion, lowered priority of tiny_dma_set_mode_x; looks like it's stopped the problem of "too much switching drops packet
    Former-commit-id: c5e94e681248877ae4711d65b96203fb6f01dd9c
2017-02-09 Starting up driver doesn't block GUI execution (Windows only).
    Bonus: "Device Disconnected" prompt works again!
    Former-commit-id: f8d3ae9bc520d8bda2fa27d74ff8d29f7aaedac2
2017-02-09 Changed Framerate to 30FPS; fixed autogain bug; removed QCP2 crashes
    30FPS gives 2% CPU usage on a 2600k@4.8; ~10% of one core.
    QCPP2 is not enabled since performance is kak on Qt 5.7.
    Former-commit-id: bfb2935812be8b81271fa2ebf17cfdcb7cffd337
2017-02-18 Fixed little PCB glitch
    Pre-compiled stuff all changed due to move from Qt 5.7.0 to Qt 5.7.1
    Former-commit-id: 3ddc37a4b541574c264f5d0a22a641fb5395630c
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2017-04-09 Fixed occasional corruption (Windows Only)
    Also small fix for doubled sample rate.
    Former-commit-id: 642f0c6d7f10ebe8f0e5992640ebd3745c563d03
2017-05-25 Bugfix: CH2 was fetching singleBit samples on CH1 mode being == 2.
    Former-commit-id: 9f6f5695fdb75544451091c9dc2016cfb2135f19
2017-06-02 Added "bad connect detection" (frame phase error detection) to Unix.
    Also changed compiler flags so that optimisations don't wreck the for
    loop when initialising the pipe IDs. Hopefully this fixes Android as
    Q_debugstream has a slight change just so that gcc doesn't get upset.
    Former-commit-id: f7ddf6ae054d4e6ac89ce757fdfdfd5c28bc936c
    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
2017-06-02 Temporarily desabled frame phase error code. Gets false positives.
    Former-commit-id: 69d72b19f300efcdf109f4d32ffa95573e8f4a04
2017-06-19 Android reinit fine as long as device doesn't reconnect before destructor called
    Former-commit-id: 09e3568605766a7b690037b14bc0fbe67e0e3e26
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2017-06-29 Capacitance meter correctly and accurately detects rise and fall times
    Former-commit-id: 5f66ee29166221667b0ce6bd283d78f5262c83f4
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2017-10-21 Cleaned junk out of repo.
    Still need to edit history
    Former-commit-id: e2061432d4b3d2bbb1f9621f3cce34d43b682b2a
    Former-commit-id: aeeed8aa2af692f92b7ea7ec8cc042d49c679ce5
    [Tinylab_proto1.csv, Tinylab_proto1.drl, Tinylab_proto1.dsn, Tinylab_proto1.kicad_pcb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]
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2018-04-07 librador_get_iso_data now returns volts (plus other minor fixes)
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2018-07-29 PCB Eschema updated to KiCAD 5.0 format and missing values filled in
    [Tinylab_proto1-2018-07-29-16-12-45.sch, Tinylab_proto1-2018-07-29-18-57-28.sch, Tinylab_proto1.sch]
2018-11-21 Add AltiumPCB design
    [Analog.SchDoc, Labrador.SchDoc, PCB.PcbDoc, Power.SchDoc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]
2018-11-22 Add generated schematic, BOM, gerber & NC Drill files
    [PCB-BOM.xlsx, PCB.GBL, PCB.GBO, PCB.GBP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]
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2019-01-23 Isobuffer refactor (#64)
    * make isobuffer.cpp follow the common bracket style
    * Add a few utility functions to isoBuffer, and reorganize and comment isobuffer.h
    * refactor a few functions in isoBuffer using the newly added functions
    * Clean up isoBuffer::readBuffer. Requires particular attention during review
    * remove unused variable isoBuffer::firstTime
    * Fix formatting and add a comment to isoBuffer::maybeOutputSampleToFile
    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
2019-03-18 Uartstyledecoder refactor (#72)
    * fix brackets
    * make serialBuffer a member of uartStyleDecoder and add m_ prefix, loosen synchcronization on updateConsole
    * make uartStyleDecoder::updateTimer a member variable
    * write isEvenParity lambda in a more concise way
    * add unused attribute on decode_baudot. make isEvenParity take an argument
    * add const where possible on uartStyleDecoder methods
    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
